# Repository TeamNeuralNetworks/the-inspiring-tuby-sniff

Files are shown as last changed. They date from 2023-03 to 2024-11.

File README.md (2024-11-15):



# tuby-sniff
An anesthesia mask adapted to mice for stereotaxic devices.

Ready-to-print CTB files are here + instructions to build the system (How to build your amazing Tuby-Sniff).

Designed for the 3D printer ELEGOO MARS 2 PRO and for a biocompatible resin as the ANYCUBIC ECO Plant-base 405nm UV RESIN BLACK (color adapted to see better the slices).

The different steps to build the tuby-sniff:

1-Print the different parts of the tuby-sniff. If you try to make a new .ctb file using chitubox, make sure to give an angle of 9° (head down) and a z-lift height of 2mm for the tuby-sniff_head and tuby-sniff_arm. Otherwise the prints will be quite odd. For the tuby-sniff_pivot, it should be print vertically. 

2-Wash the different parts. Since there is small holes in the head and arm, everything should be washed carefully. Then rub a bit of alcohol on the different pieces to remove all the resine and make sure to remove everything in the holes with a needle. Then make them dry.

3-Cure the parts during 3 minutes. If the pieces are not washed enough they will be sticky. You could try to rub a bit of alcohol to remove that. If the pieces were not dried enough, there will be some white spots here and there.

4-Assemble the tuby-sniff. Quite easy, put the arm and the head together and then insert the pivot. Then, put super-glue on the outside of the arm and pivot. But not on the head and on the holes.

5-Add the tubing to the tuby-snif. Cut two 10cm-long plastic tubes of 1mm of diameter, insert then in the two holes of the head. Try to get only 3mm of tubes inside the head, then use super glue to fix the tubes on the head. 

6-Add adaptators. Insert a 10uL pipette tip at each tube's end. Then use super glue to fix the junction.

7-Craft a stop rod. For that use a 23Gx1" (0.6x25) needle, cut the sharp end.

Now you can orient the tuby-sniff head as you want and fix it by inserting the stop rod in the holes present on the tuby-sniff arm. 

Created and designed by Anthime Perrot.

Tuby-sniff with cone head


Ready-to-print file with standard head


Fusion 360 file 


Tuby-sniff © 2023 by Anthime Perrot is licensed under CC BY 4.0 .

If my device helped you in your project, please cite this repository. 

Anthime Perrot,PhD Student,

Institute of Cellular and Integrative Neuroscience, INCI UPR 3212

This work was funded by the European Research Council, Grant agreement ID: 101042329.

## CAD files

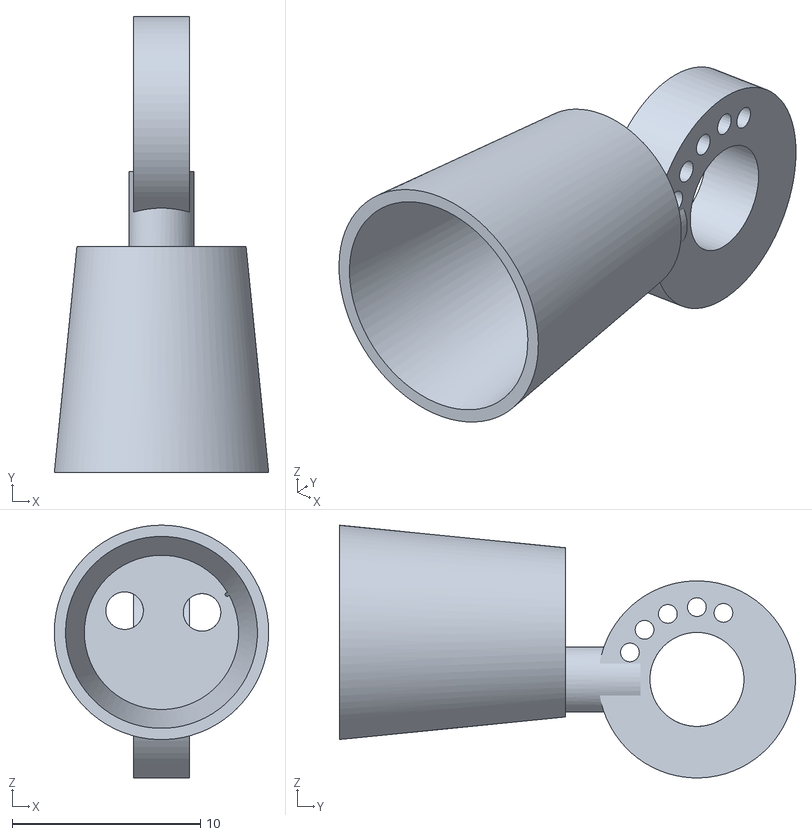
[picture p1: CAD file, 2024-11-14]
3D_objet/tuby-sniff_cone_head.stl
11.4 x 24.2 x 13.4

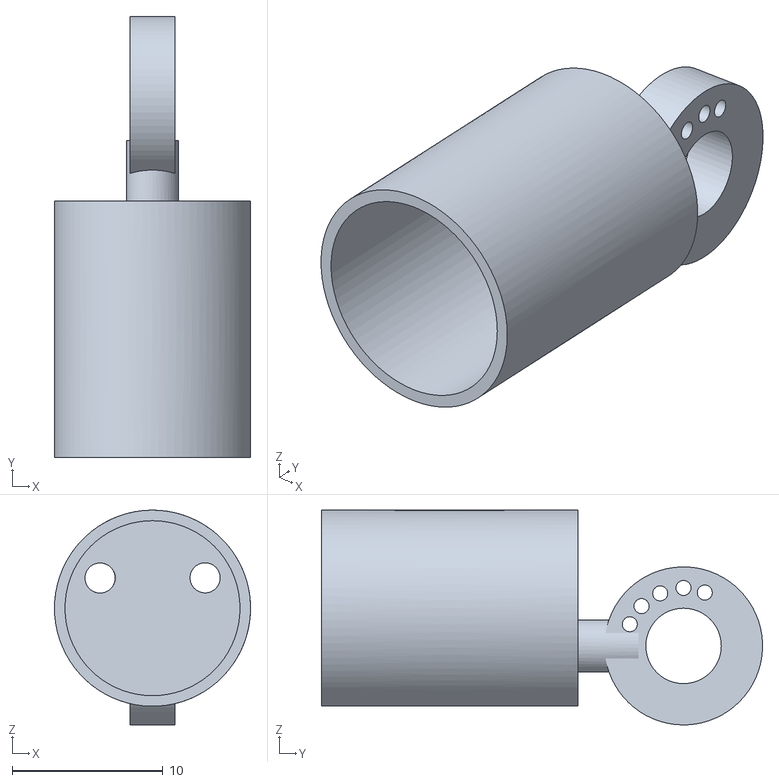
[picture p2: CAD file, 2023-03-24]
3D_objet/Tuby-sniff_head.stl
13.0 x 29.2 x 14.2

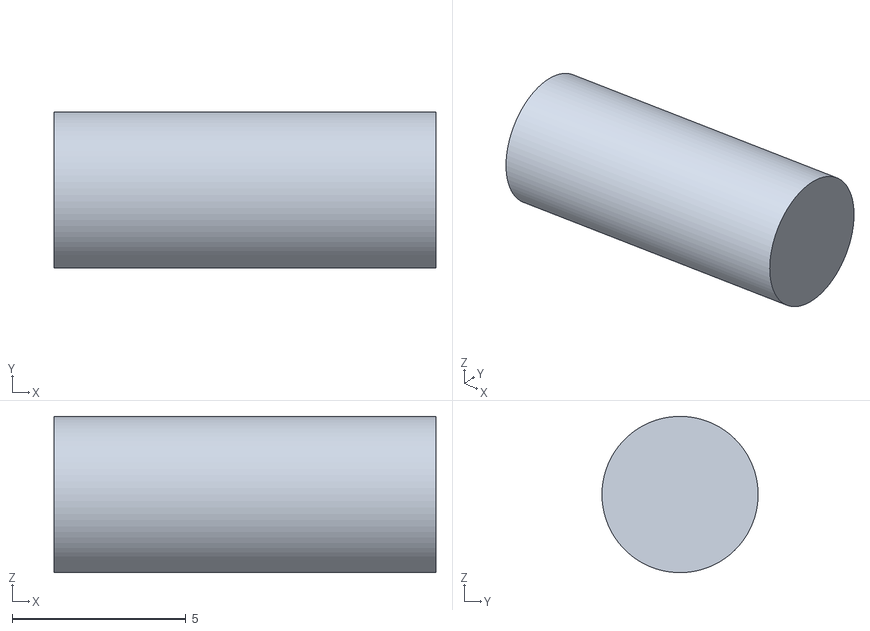
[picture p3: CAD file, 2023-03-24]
3D_objet/Tuby-sniff_pivot.stl
11.0 x 4.50 x 4.50

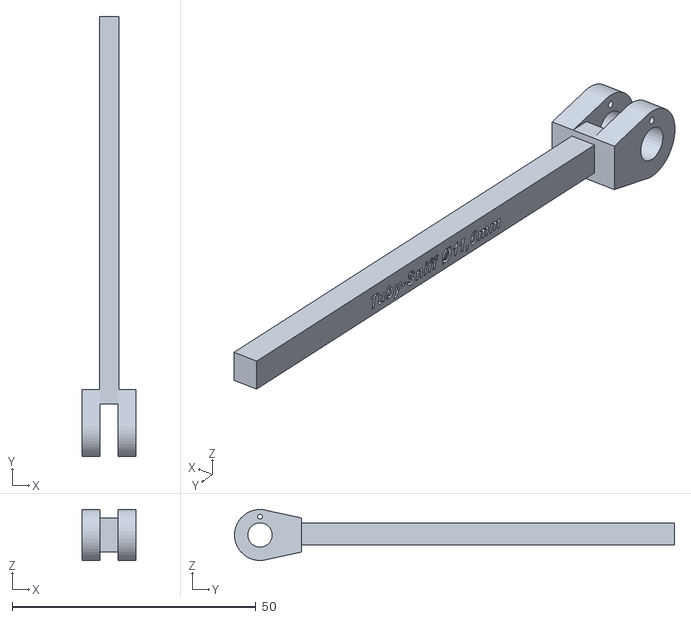
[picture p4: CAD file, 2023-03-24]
3D_objet/Tuby-sniff_arm.stl
11.0 x 90.2 x 10.5

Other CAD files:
3D_objet/Tuby-sniff_Ø11_6mm .f3d
3D_objet/tuby-sniff_cone_head.f3d

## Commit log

2023-04-13 mauvais model
    [Tuby-sniff_Ø11_6mm .f3d, Tuby-sniff_Ø11_6mm.f3d]
2024-11-14 cone head
    [tuby-sniff_cone_head.f3d, tuby-sniff_cone_head.stl]

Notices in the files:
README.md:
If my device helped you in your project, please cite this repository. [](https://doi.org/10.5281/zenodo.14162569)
